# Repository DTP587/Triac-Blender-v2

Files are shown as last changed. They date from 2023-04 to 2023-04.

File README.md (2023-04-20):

# Triac Blender
_Blender with Triac v1, Build Notes. Part of the Open Science Framework repository [OpenLPE](https://osf.io/evupy/)_

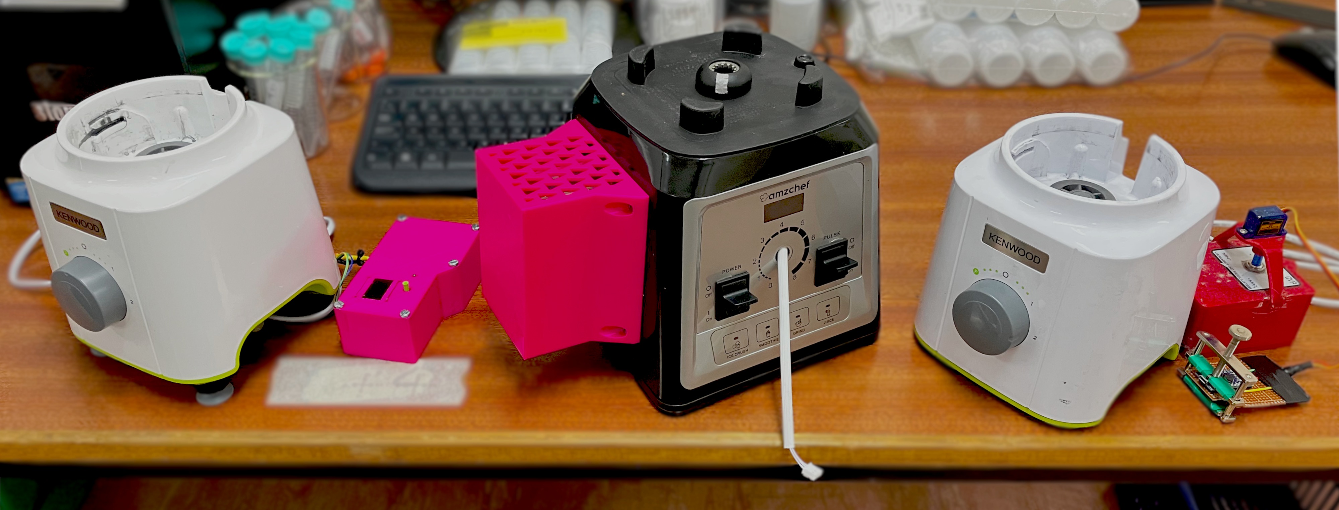
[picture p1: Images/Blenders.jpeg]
Image of all three blenders in order


_From right to left, Triac-Blender v1, Triac-Blender v2, PID-Blender._

### Background \& Motivation

_This is part of the [OpenLPE](https://osf.io/evupy/) labware project._

There are no reasonably priced commercial blenders with adequate speed control for practical experiments. The closest is the [Waring LB20ES](https://www.thelabstore.co.uk/waring-lb20es-variable-speed-control-blender-1-0-litre-stainless-steel-container-230v-50-hz-ce-approved-rohs-with-european-f-schuko-plug.html), being over £1000. This left us feeling priced out, so we had to come up with an alternative, which is this Triac modification, enabling for great power selectivity. Speed on this version is much more repeatable and reliable as we are selectively controlling how much power is delivered, which cures a lot of the problems of the v1 blender. The issue here is that there is no On/Off functionality, so short bursts at high speed or long bursts at low speeds are the only way this one can be run at the moment.

_The little wire hanging out of the dial position in the photo of the blender above? Thats the x2 hal effect sensors which come already installed!_

The blenders I have been controlling range between $600$ $W$ to $2$ $kW$ peak power, which they can sustain for a maximum of $\approx 1$ $min$ before they get dangerously hot (and melt-y). Some come with automatic sensors to detect when they are overheating and shut-off automatically to save the motor. From my testing, I recommend following the manufacturer's recommendations alternating running it for $1$ $min$ **ON** with a subsequent minimum of $1$ $min$ **OFF** to allow it to cool down.

### Disclaimer!

Playing with AC is _incredibly_ dangerous. Make sure to take all precautions when making modifications and ensure everything is unplugged and grounded.

## Potential Changes

List of changes and whether they have been implemented.

- [ ] Could add in arduino functionality at a later date, would allow for On/Off Control.

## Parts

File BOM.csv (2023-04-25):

Item | Link | Qty | Price per Unit | Cost | Description
AMZChef NY-8088MJD | https://www.amazon.co.uk/Smoothie-AMZCHEF-Commercial-Container-25000RPM/dp/B08CKTB6Z4 | 1 | £150.00 | £150.00 | Top of the line commercial blender, resistant to some solvents.
Walfront Dimmer Circuit | https://www.amazon.co.uk/Digital-Voltage-Regulator-Control-Thermostat/dp/B076VKJM42 | 1 | £17.43 | £17.43 | Easy to use, and has the potential for wiring in a separate board.
Heat Shrink |  | - | - | - | To protect soldered collections.
Soldering iron |  | - | - | - | Solder wires together.
Aluminium Foil |  | - | - | - | To isolate the Snubber circuit from the arduino.
Red wire 20 awg | https://www.amazon.co.uk/Electrical-Wire-AWG-Extension-Brightfour/dp/B07CGKCJFV | - | - | - | Live wiring, of good gauge to handle the current.
Black wire 20 awg | https://www.amazon.co.uk/Electrical-Wire-AWG-Extension-Brightfour/dp/B07CGKCJFV | - | - | - | Neutral wiring, of good gauge to handle the current.
3DP Bolt-on box |  | - | - | - | To isolate the live AC and be a little safer, also allow a little airflow.
3DP Backing Plate |  | - | - | - | To eliminate the need for nuts to fix in the bolt-on box
M4 countersink 15 mm | https://uk.rs-online.com/web/p/socket-screws/0171837 | 6 | £0.20 | £1.20 | To bolt the Pink box lid shut.
 |  |  |  | £168.63

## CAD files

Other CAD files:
CAD/AMZchef Power Board Enclosure.f3d

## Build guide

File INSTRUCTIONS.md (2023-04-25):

# Build Instructions and Notes

### Operating Principles

This project involves the [phase-angle control](https://electricalacademia.com/electronics/scr-thyristor-phase-control-circuit/) of AC signals. this allows for accurate power delivery but it is important to remember that rotational speed of the blender $\neq$ power.

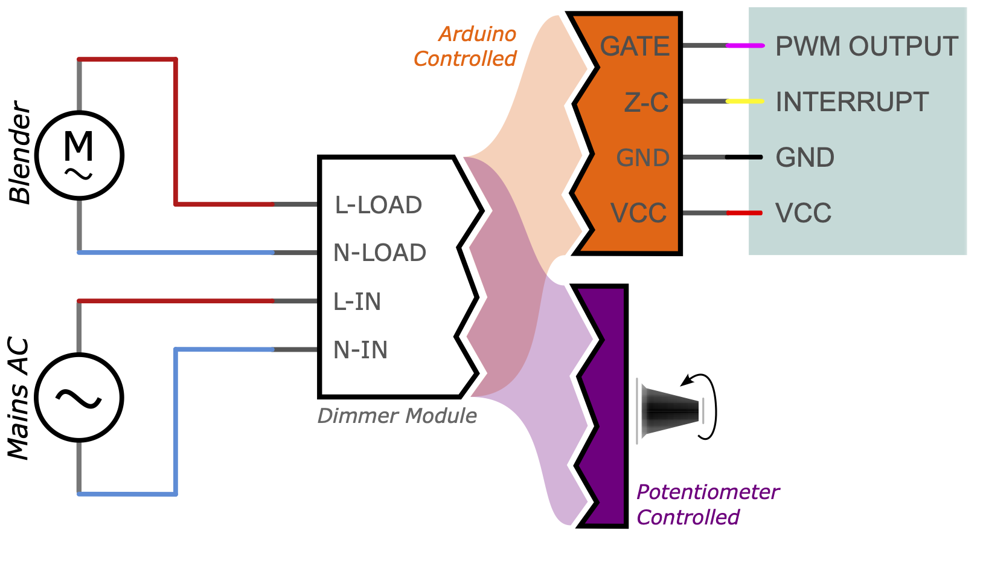
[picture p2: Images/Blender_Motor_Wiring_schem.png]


_Very basic wiring of a dimmer module with potentiometer control or arduino control, depending on the circuit._

This particular build is a step between potentiometer and arduino control, as the dimmer module comes in two parts; a screen with tactile switches effectively acting as an arduino, and a dimmer module with an arduino interface. The markings on the back of the screen state SCR (GATE), ZERO (Z-C), GND and 5V (VCC). So effectively one could replace the screen with an arduino to achieve Phase Angle Control directly.

Note also, that I found it possible to measure the speed simply from the noise given off by the blender with the [spectroid app for android](https://play.google.com/store/apps/details?id=org.intoorbit.spectrum). Will take some work to recognise which signals are which, but if you are uninterested in exact speed, you can make the setup more repeatable by aiming for previously obtained resonant frequencies!

##### Phase Angle Control

Phase angle control, is a method of controlling the duty cycle of an AC signal every half cycle. This typically uses a triode called a triac sometimes also called a Silicon Controlled Rectifier (SCR) or a Thyristor, and you will often see these terms banded around when shopping circuitry. The circuit is similar to what you would find in a dimmer switch in a house, hence sometimes it is called a dimmer or dimming circuit.

The main advantages to this type of rectification compared to other similar functioning circuits is that:

1. It does not disapate very much energy.
2. Simple to implement.
3. Duty cycle is small for mains AC (100% $\sim 10\;ms$), so the power delivery is pretty constant (no flickering).



_[Simple representation of phase angle control.](https://www.libratherm.com/phase-angle-control-vs-zero-crossover-control/)_

The AC signal in potentiometer controlled cases is routed through a voltage divider which feeds into the GATE pin of the Triac. The exact electronics and some of the issues surrounding these circuits is well discussed in [this article](https://eepower.com/technical-articles/alternating-current-ac-load-control-with-triacs/#). In arduino controlled units, there will be some sort of isolation between the low and high voltage side, primarily through the use of an optocoupler or [similar circuitry](https://www.circuitar.com/nanoshields/modules/triac/).

The original circuitry on the blender used here is a less precise "Burst firing" control, where multiple periods of AC are allowed through at a time, effectively meaning the regulation cycle is much longer than that achievable by Phase angle Control.

## Bill of Materials

|Item                   |Link                                                                                 |Qty|Price per Unit|Cost   |Description                                                               |
|-----------------------|-------------------------------------------------------------------------------------|---|--------------|-------|--------------------------------------------------------------------------|
|AMZChef NY-8088MJD     |https://www.amazon.co.uk/Smoothie-AMZCHEF-Commercial-Container-25000RPM/dp/B08CKTB6Z4|1  |£150.00       |£150.00|Top of the line commercial blender, resistant to some solvents.           |
|Walfront Dimmer Circuit|https://www.amazon.co.uk/Digital-Voltage-Regulator-Control-Thermostat/dp/B076VKJM42  |1  |£17.43        |£17.43 |Easy to use, and has the potential for wiring in a separate board.        |
|Heat Shrink            |                                                                                     |-  |-             |-      |To protect soldered collections.                                          |
|Soldering iron         |                                                                                     |-  |-             |-      |Solder wires together.                                                    |
|Red wire 20 awg        |https://www.amazon.co.uk/Electrical-Wire-AWG-Extension-Brightfour/dp/B07CGKCJFV      |-  |-             |-      |Live wiring, of good gauge to handle the current.                         |
|Black wire 20 awg      |https://www.amazon.co.uk/Electrical-Wire-AWG-Extension-Brightfour/dp/B07CGKCJFV      |-  |-             |-      |Neutral wiring, of good gauge to handle the current.                      |
|3DP Bolt-on box        |                                                                                     |-  |-             |-      |To isolate the live AC and be a little safer, also allow a little airflow (Both printed components are contained in the same .f3d archive file).|
|3DP Backing Plate      |                                                                                     |-  |-             |-      |To eliminate the need for nuts to fix in the bolt-on box (Both printed files are contained in the same .f3d archive file).                 |
|M4 countersink 15 mm   |https://uk.rs-online.com/web/p/socket-screws/0171837                                 |6  |£0.20         |£1.20  |To bolt the backing plate to the Dimmer and                                                      |
|                       |                                                                                     |   |              |£168.43|                                                                          |

## Mods

There are no direct modifications to the blender itself, apart from wiring in the dimmer module. In this case, a little fitting is needed in order for everything to sit nicely within the blender.

Firstly, we removed the blender control board from the front of the blender, effectively removing any interference from the on-board electronics, this can then be discarded. In this blender, there is a bespoke power management IC in order to power the blender and the control board. We do not require this board for the blender to function, so it can be removed, we opted for it to stay in there, as it gives us some flexibility to use the on-board switches later. Much like in the previous version, we're looking to follow the same steps as the v1 blender, by wiring the dimmer module between the motor and mains AC.

### Wiring

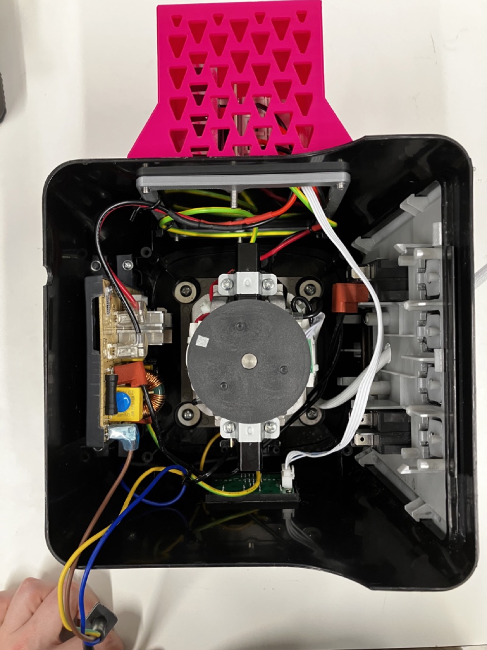
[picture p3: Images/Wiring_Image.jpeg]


_Blender with modifications, opened from above._

In the above; Live (brown), Ground (Yellow), Neutral (Blue) are routed into the blender from the bottom left. Neutral and Live are wired into the power IC (left side of the blender), while ground is connected to the cast motor mounting. The signal is filtered, passed through the main switch (right side of the blender) and then fed back into the power IC.

After, Live and Neutral are routed to the top of blender through a hole to the dimmer module on that side (obscured by the 3D printed bolt-on box). Ground is also wired through to the Dimmer module so that the electronics share a common ground.

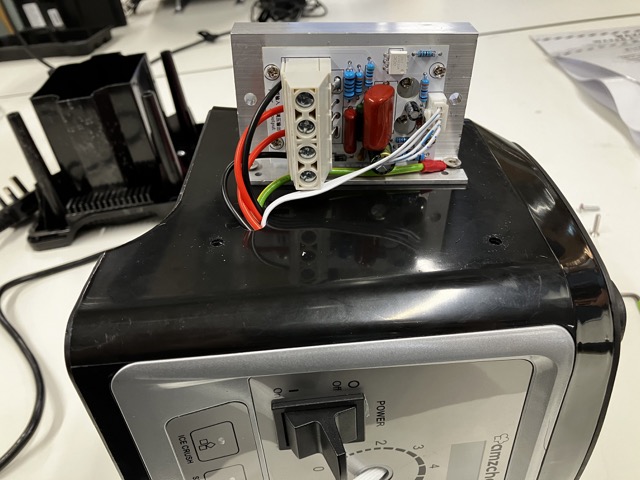
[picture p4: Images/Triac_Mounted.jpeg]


_Dimmer module, mounted to the side of the blender_

Motor live, motor neutral, mains live and mains neutral (after passing through the power management IC) are all passed into the board, and the board is grounded using one of the two M4 countersink bolts used to attatch the dimmer module to the blender. The control signal is passed via the white cable down to the screen module, which is glued in place (bottom of the blender in the first image of this section). The 3D printed enclosure sits above and is fixed in place using 4 M4 countersink bolts.s

### Future Modifications

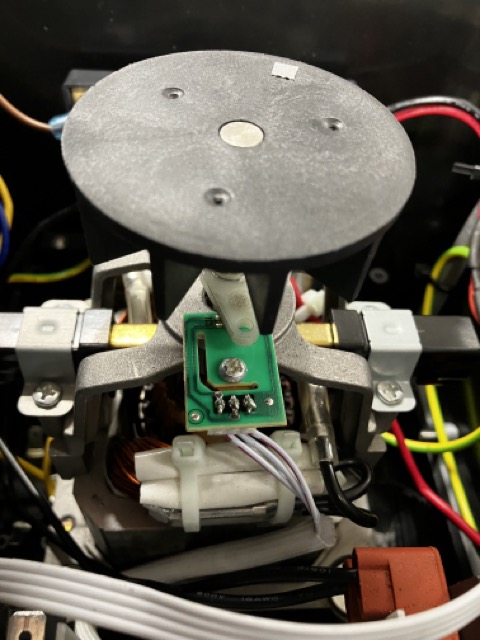
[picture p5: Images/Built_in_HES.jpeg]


_Builtin Hall-Effect Sensor, with two magnets, should allow for very precise speed measurements up to high rpms._

As noted before, there stands a lot to be modified with this setup, it offers a range of features including on-board power management and speed sensing, and with a small amount of effort, could be made into a completely autonomous blender.

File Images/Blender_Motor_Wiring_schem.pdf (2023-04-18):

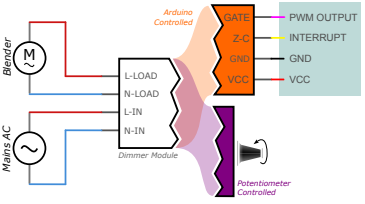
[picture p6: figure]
L-LOAD; N-LOAD; Blender Mains AC; Potentiometer Controlled; Dimmer Module; Arduino Controlled; VCC; PWM OUTPUT; INTERRUPT; GND; GATE
